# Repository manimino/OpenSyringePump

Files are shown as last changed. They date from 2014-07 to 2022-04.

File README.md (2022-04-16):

# Open Syringe Pump

Deliver small, accurate amounts of liquid. Good for food engineering, CNCs, and bioscience. Cheaper and more flexible than the $1000+ commercial solutions.

This was the first open-source syringe pump, back when 3D printing and open-source hardware took off circa 2015. It saw practical use in many lab and hobby environments. I personally used it in [animal training experiments](https://github.com/manimino/ShrewDriver) to deliver juice rewards.

Successors improved on this design substantially. If you're making a new syringe pump, go find a newer design instead. This repo's for legacy reasons now, to support anyone with one of these pumps.

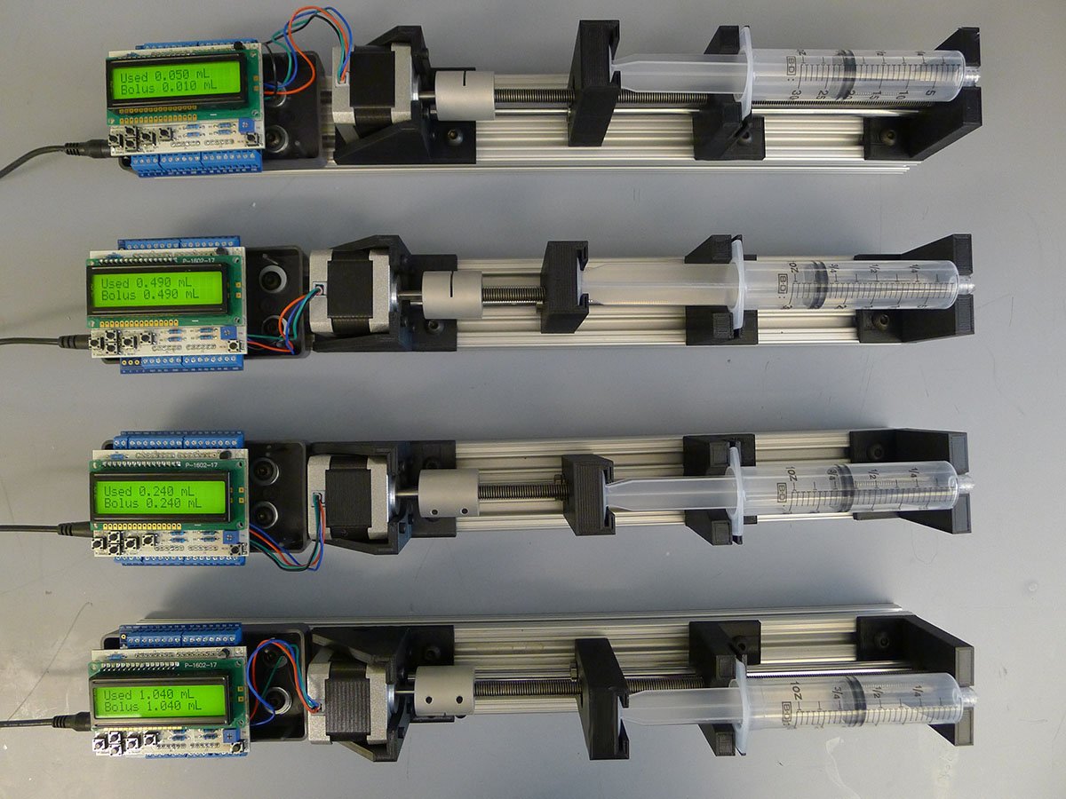
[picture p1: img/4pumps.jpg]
4 syringe pumps

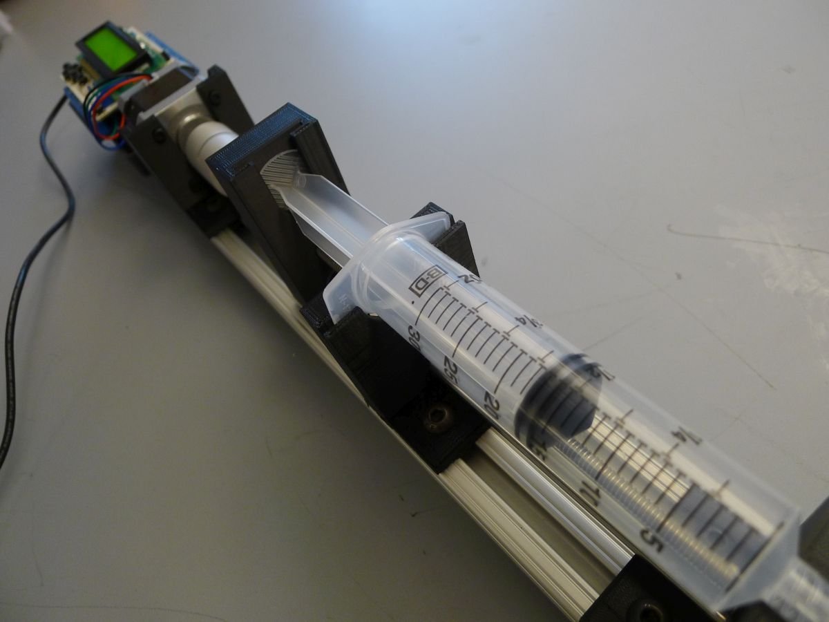
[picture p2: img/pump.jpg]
left side

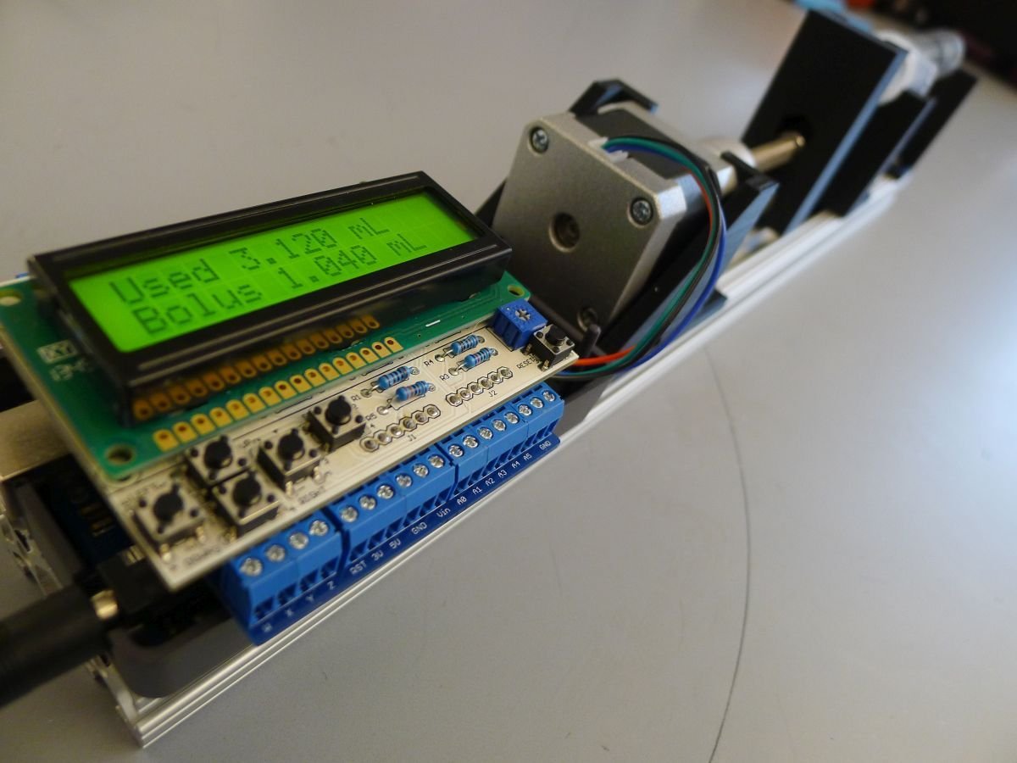
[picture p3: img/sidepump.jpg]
right side


If you want to build one, refer to the [Assembly instructions](instructions.md) and [Electronics + Printing doc](./Syringe%20Pump%20Guide.docx).

## Usage

The face buttons provide manual operation - adjust bolus size and push / pull.

It can be triggered to push and pull liquid via the digital pin inputs, and it accepts more complex commands via serial over USB. 

## Code Layout

'3D files' contains OpenSCAD and STL files for customizing and printing the plastic pieces.

'syringePump' contains the Arduino code.

It requires the AccelStepper library, which you can find in the 'libraries' dir. Copy it into your Arduino\libraries directory to use. You can also get the library from the author's page here: http://www.airspayce.com/mikem/arduino/AccelStepper/

##  Materials

The total cost should come out to about $250 with shipping. So, that's 
substantially cheaper than a commercial syringe pump; they typically go 
for $1000+.

Cost is not the only concern, though. What you get with this thing is:

**- Hackability:** Open-source software and hardware all the way. Customize the hardware and software to do anything you need.

**- Modularity:** You can swap out each component for another one of your choosing. Exceptions and concerns noted below.

**- Extendability:** Want to add [Ethernet]http://arduino.cc/en/Main/ArduinoEthernetShield) or [Bluetooth]http://www.adafruit.com/product/1628)? Both shields are compatible, just stack them on. This [SD card shield]https://www.adafruit.com/product/1141) is compatible too if you want to add data logging. 

**- Ease of assembly:** Minimal soldering required, and tutorials + vendor support are available for most components.

**- Availability of components:**
 Everything's off-the-shelf from stable sources (Adafruit, SparkFun, 
Amazon, McMaster-Carr). If you're in the US, all parts should arrive in 
well under two weeks.

## Electronic Components:

| Purpose                          | Product Link                                                               | Vendor   | Cost (not including shipping) | Notes                                                                                                                      |
|----------------------------------|----------------------------------------------------------------------------|----------|-------------------------------|----------------------------------------------------------------------------------------------------------------------------|
| Microcontroller                  | Arduino Uno R3                                                             | Adafruit | $24.95                        | --                                                                                                                         |
| Stepper Motor                    | NEMA 17 stepper motor, 12V, 1.3A, Holding Torque 40N*cm. Model 42HS4013A4. | Adafruit | $18.50                        | Plenty of power for pushing even thick liquids.                                                                            |
| Stepper Motor Driver             | Big Easy Driver                                                            | Sparkfun | $14.95                        | Attach to digital pins 2 and 3.                                                                                            |
| User Interface Shield            | LCD button shield                                                          | Sparkfun | $12.95                        | Uses digital pins 4 through 9.                                                                                             |
| Power Source                     | 24V 1A power supply                                                        | Jameco   | $11.95                        | --                                                                                                                         |
| Power Switch                     | Inline Power Switch                                                        | Adafruit | $2.50                         | --                                                                                                                         |
| Power Jack                       | Terminal Power Jack                                                        | Adafruit | $2.00                         | --                                                                                                                         |
| Enclosure                        | Arduino Project Enclosure                                                  | Amazon   | $8.95                         | Fits nicely to the Arduino and to the aluminum rail. Only the bottom half is used.                                         |
| Trigger Inputs & Driver Mounting | Proto-Screwshield (Wingshield) R3 Kit for Arduino                          | Adafruit | $14.95                        | A convenient way to expose digital pins so you can send triggers to the syringe pump. Also fits the Easy Driver perfectly. |

## Mechanical Components:

| Purpose                               | Product Link                                                   | Vendor         | Cost (not including shipping) | Notes                                                                                                                                                           |
|---------------------------------------|----------------------------------------------------------------|----------------|-------------------------------|-----------------------------------------------------------------------------------------------------------------------------------------------------------------|
| Mounting Rail                         | 18-inch piece of 1"x2" 80/20 extruded aluminum rail.           | Amazon         | $8.97                         | Mounting everything on the rail makes the project modular and space-efficient. And the 18" length means your syringe pump will fit into most rack mount setups. |
| Motor mount                           | STL + SCAD file (GitHub)                                       |                | --                            | 3D printed                                                                                                                                                      |
| Syringe plunger attachment            | STL + SCAD file (GitHub)                                       |                | --                            | 3D printed                                                                                                                                                      |
| Syringe barrel holder                 | STL + SCAD file (GitHub)                                       |                | --                            | 3D printed                                                                                                                                                      |
| Syringe tip holder                    | STL + SCAD file (GitHub)                                       |                | --                            | 3D printed                                                                                                                                                      |
| Nuts and bolts for attaching to 80/20 | 80/20 Attachment Nuts and Bolts, Economy, 25-pack              | Amazon         | $10.00                        | Cheap and effective.                                                                                                                                            |
| Shaft coupler                         | 5mm - 8mm Rigid Coupling 25x30mm For CNC Stepper Motor ST-RC03 | Stepper Online | $7.47                         | Attaches the stepper motor to the threaded rod.                                                                                                                 |
| Threaded Rod                          | M8 Threaded Rod, Type 316 Stainless Steel, 1m length           | McMaster-Carr  | $14.72                        | Comes as a 1m stick. You'll want to cut this down to around 300mm. There are many ways to do this; I used a chop saw.                                           |
| M8 Nut for Threaded Rod               | M8 Nut, Type 316 Stainless Steel, 50-pack                      | McMaster-Carr  | $13.38                        | --                                                                                                                                                              |
| Smooth rod                            | 8mm rod, 330mm long                                            | Amazon         | $13.39                        | --                                                                                                                                                              |
| Linear Bearing                        | LM8UU 12-pack                                                  | Amazon         | $13.00                        | --                                                                                                                                                              |
| Syringe                               | 30mL syringe 5-pack                                            | Amazon         | $7.99                         | --

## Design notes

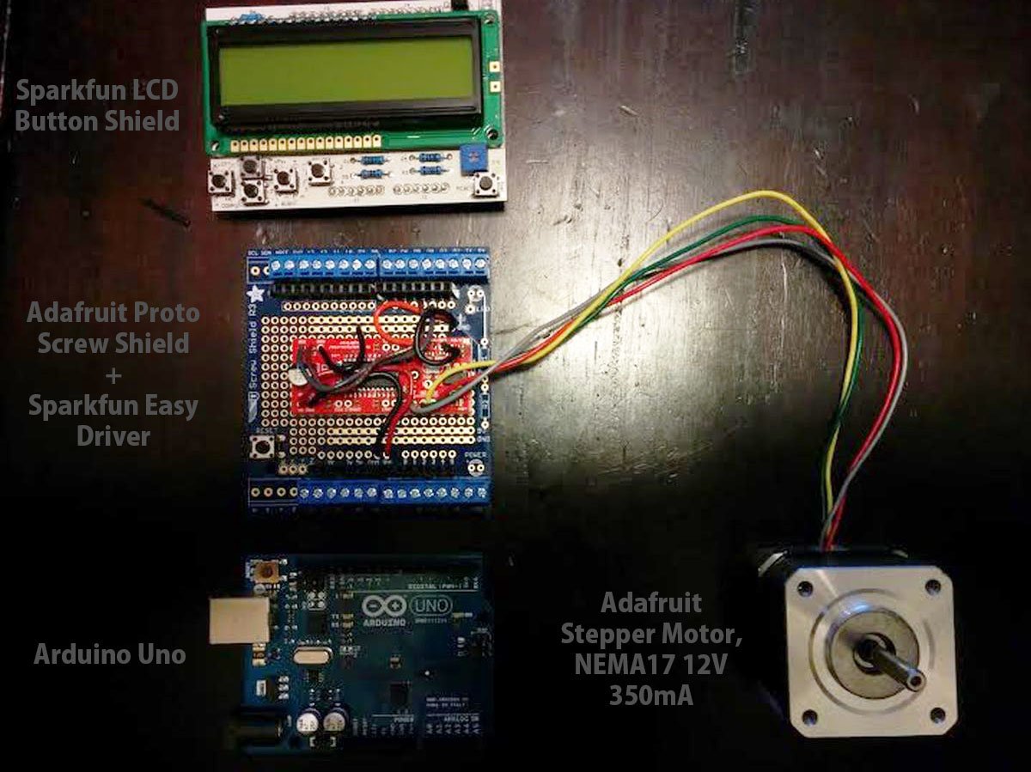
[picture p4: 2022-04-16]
img/electronics.jpg

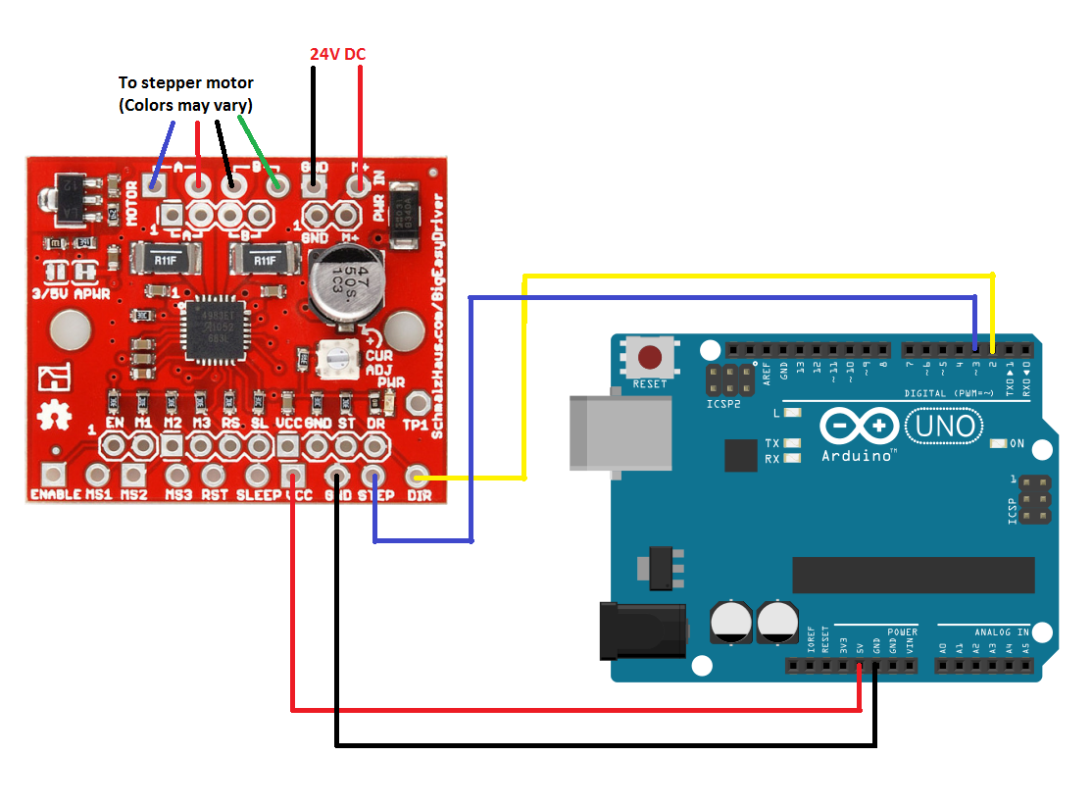
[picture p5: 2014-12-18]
diagrams/24V_BigEasyDriver.png

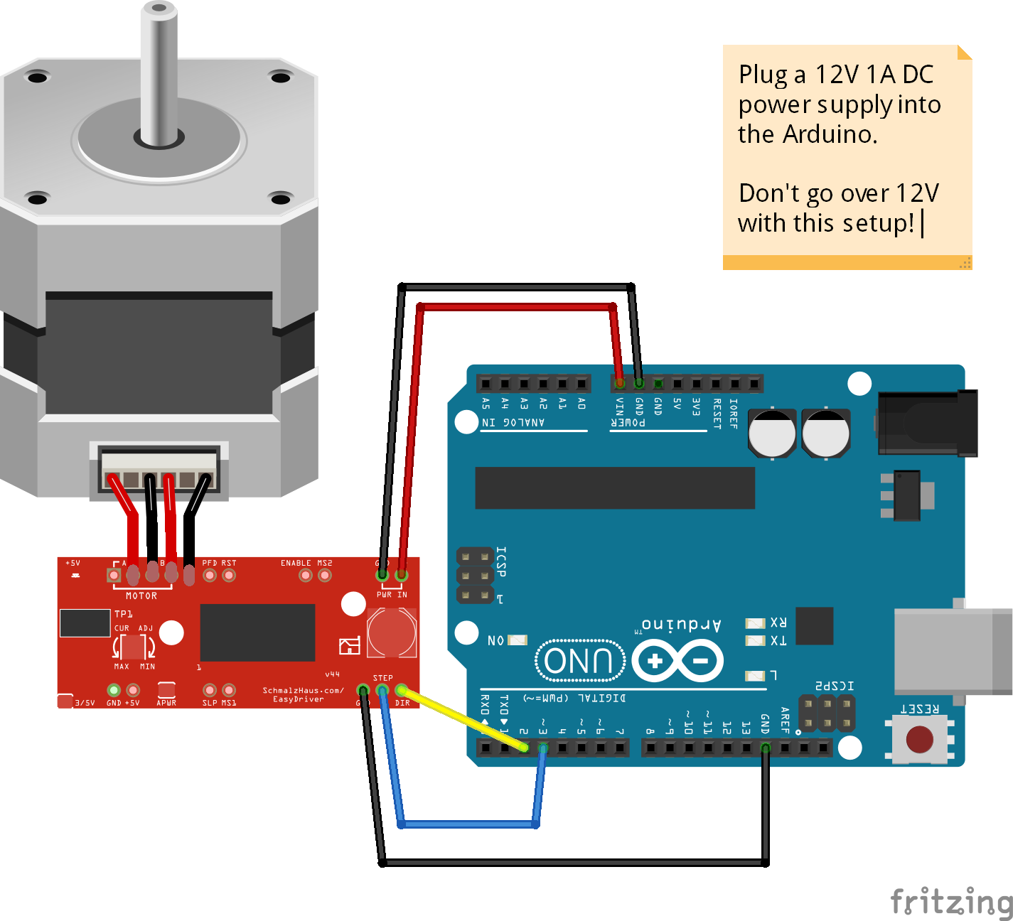
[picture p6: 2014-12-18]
diagrams/12v-easyDriver_bb.png

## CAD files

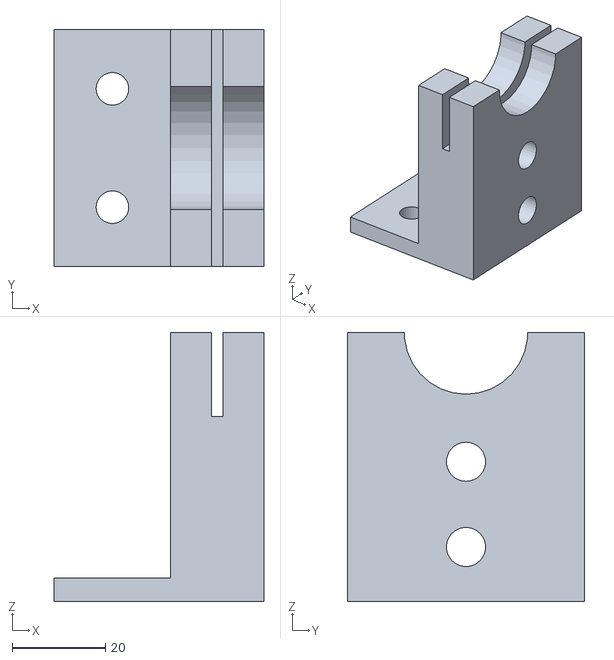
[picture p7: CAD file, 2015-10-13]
3D Files/rodMountBarrel.stl
45.0 x 50.8 x 57.8

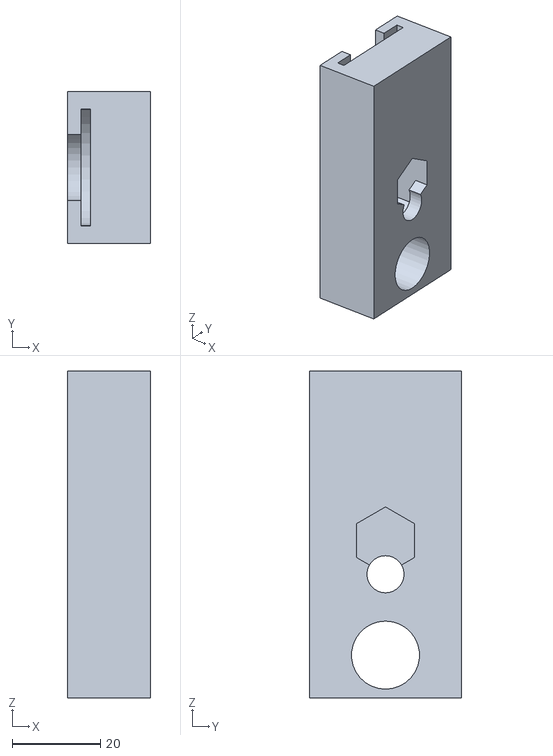
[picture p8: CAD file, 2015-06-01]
3D Files/rodMountPlunger.stl
18.8 x 34.5 x 74.0

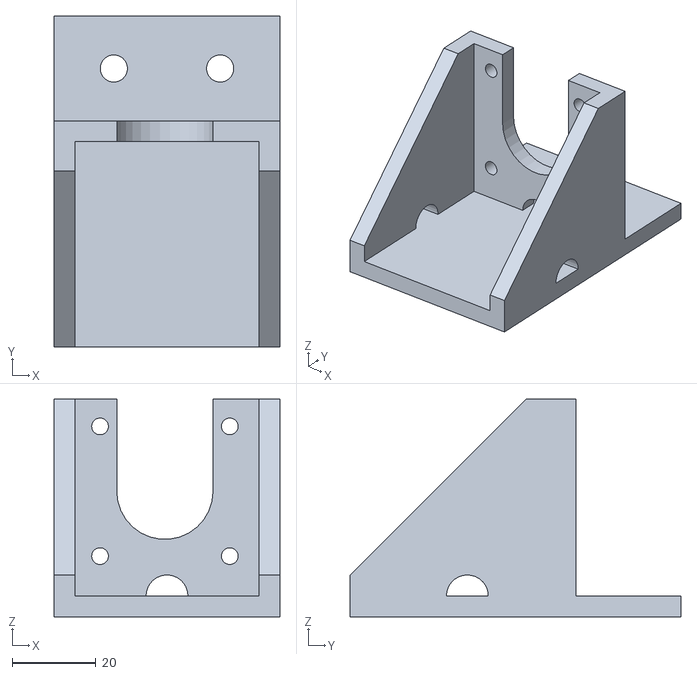
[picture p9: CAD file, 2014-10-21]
3D Files/nemaMount.stl
54.0 x 79.0 x 52.0

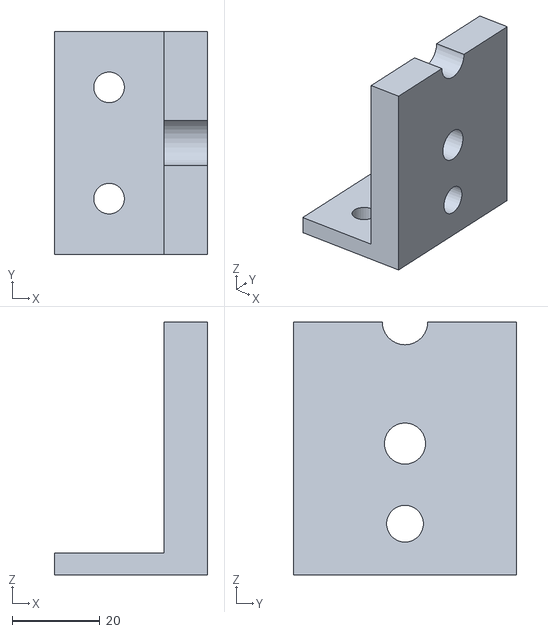
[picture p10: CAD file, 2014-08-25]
3D Files/rodMountSyringe.stl
35.0 x 50.8 x 57.8

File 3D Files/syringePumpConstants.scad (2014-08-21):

/* === Project-universal Constants === */

//Not all of these variables are used in this specific model,
//but the same variable set is used across all models in this project.

$fs = 0.1;

inch = 25.4; //for mm conversion

//width of base
baseSizeY = 2*inch;
centerY = baseSizeY / 2; //both axes go right down the middle of the base

//stepper motor
stepperZSize = 42;
stepperYSize = 42;

//608 bearing 
bearing608Height = 8.5;
bearing608Diameter = 22.5;

//height of holder for 80/20 screws
mountPlateHeight = 5;

//axis heights
threadedAxisHeight = stepperZSize/2 + mountPlateHeight + 4;
smoothAxisHeight = (threadedAxisHeight-6.6) / 2;
smoothRodRadius = 4.2;

//syringe properties
barrelDiameter = 25;

barrelSlotThickness = 3;
barrelSlotHeight = 28;

syringeCenterHeight = threadedAxisHeight + bearing608Diameter/2 + 4 + barrelDiameter/2;

//fixes render oddities
floatCorrection = 0.001; 
floatCorrection2 = 2*floatCorrection; 

//8020 mounting plate
screwPlateSize = 25;	
screwRadius = 3.5;

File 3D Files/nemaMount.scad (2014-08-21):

include <syringePumpConstants.scad>

nema_17_mount();

module nema_17_mount()
{
	wall_thickness = 5;
	motor_width = 42;
	frame_width = motor_width + (wall_thickness + 1)*2;
	bolt = 4;
	height = 25;

	inch = 25.4;
	screwPlateSize = 25;	
	screwRadius = 3.25;
	
	//these are all the mount point holes.
	x1 = -wall_thickness;
	y1 = wall_thickness*2;
	x2 = frame_width+wall_thickness;
	y2 = wall_thickness*2;
	x3 = -wall_thickness;
	y3 = frame_width-wall_thickness*2;
	x4 = frame_width + wall_thickness;
	y4 = frame_width-wall_thickness*2;
	
	//center the whole thing in X
	translate([-frame_width/2, 0, 0])
	{

		//floor, with mounting holes for 80/20
			
		translate([0,-screwPlateSize,-wall_thickness]){
			difference(){
				cube(size=[frame_width,frame_width+screwPlateSize,wall_thickness]);
				
				translate([frame_width/2-inch/2, screwPlateSize/2, 0]){
					cylinder(h=wall_thickness, r=screwRadius);
				}
				translate([frame_width/2+inch/2, screwPlateSize/2, 0]){
					cylinder(h=wall_thickness, r=screwRadius);
				}

			}
		}

		difference()
		{
			//build the main unit.
			union()
			{
				//structure
				cube([wall_thickness, frame_width, frame_width]); //front face
				cube([frame_width, wall_thickness, frame_width]); //left face
				translate([frame_width-wall_thickness, 0, 0])     //right face
					cube([wall_thickness, frame_width, frame_width]);

			}


			//front left mount hole
			echo(x1, y1);
			translate([x1, y1, 0])
			{
				cylinder(r=bolt/2, h=wall_thickness);
				translate([0,0,wall_thickness])
					cylinder(r=bolt, h=wall_thickness*2);
			}
			
			//front right mount hole
			echo(x2, y2);
			translate([x2, y2, 0])
			{
				cylinder(r=bolt/2, h=wall_thickness);
				translate([0,0,wall_thickness])
					cylinder(r=bolt, h=wall_thickness*2);			
			}
			
			//rear left mount hole
			echo(x3, y3);
			translate([x3, y3, 0])
			{
				cylinder(r=bolt/2, h=wall_thickness);
				translate([0,0,wall_thickness])
					cylinder(r=bolt, h=wall_thickness*2);
			}
			
			//rear right mount hole
			echo(x4, y4);
			translate([x4, y4, 0])
			{
				cylinder(r=bolt/2, h=wall_thickness);
				translate([0,0,wall_thickness])
					cylinder(r=bolt, h=wall_thickness*2);
			}
			
			//mount hole slits
			translate([frame_width + wall_thickness*1.5, frame_width-wall_thickness*2, wall_thickness/2])
				cube(size=[wall_thickness, 0.1, wall_thickness*3], center=true);
			translate([frame_width + wall_thickness*1.5, wall_thickness*2, wall_thickness/2])
				cube(size=[wall_thickness, 0.1, wall_thickness*3], center=true);
			translate([-wall_thickness*1.5, frame_width-wall_thickness*2, wall_thickness/2])
				cube(size=[wall_thickness, 0.1, wall_thickness*3], center=true);
			translate([-wall_thickness*1.5, wall_thickness*2, wall_thickness/2])
				cube(size=[wall_thickness, 0.1, wall_thickness*3], center=true);

			//nema 17 mount
			rotate([90, 0, 0])
			{
				translate([frame_width/2+0.5, height, -wall_thickness])
				{
					translate([15.5, 15.5, 0])
						cylinder(r=bolt/2, h=wall_thickness+1);
					translate([-15.5, 15.5, 0])
						cylinder(r=bolt/2, h=wall_thickness+1);
					translate([15.5, -15.5, 0])
						cylinder(r=bolt/2, h=wall_thickness+1);
					translate([-15.5, -15.5, 0])
						cylinder(r=bolt/2, h=wall_thickness+1);

					cylinder(r=11.5, h=wall_thickness+1);

					translate([-11.5, 0, 0])
						cube([23, frame_width, wall_thickness+1]);
				}
			}

			//back slant cutaway
			translate([0, 0, frame_width+wall_thickness])
				rotate([45, 0, 0])
					translate([-frame_width, 0, -frame_width*2])
						cube(size=[frame_width*4, frame_width*2, frame_width*4]);

			//front anti-warp circle
			translate([frame_width/2, wall_thickness*1.25, 0])
				rotate([90, 0, 0])
					cylinder(r=wall_thickness, h=wall_thickness*2);

			//middle anti-warp circle			
			translate([0, motor_width/2 + wall_thickness, 0])
				rotate([0, 90, 0])
					cylinder(r=wall_thickness, h=frame_width+1);

			//cutout / tidy up cubes.
			translate([wall_thickness, wall_thickness-0.1, -1])
				cube([frame_width-wall_thickness*2, frame_width-wall_thickness, motor_width*2]);
			translate([-frame_width/2,-frame_width/2, wall_thickness+motor_width])
				cube([frame_width*2, frame_width*2, frame_width]);
			translate([-frame_width/2, -frame_width/2,-frame_width])
				cube([frame_width*2, frame_width*2, frame_width]);
		}
	}
}

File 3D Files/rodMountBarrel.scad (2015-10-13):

include <syringePumpConstants.scad>

/* === Model-specific Constants === */

//cube containing rods and syringe barrel stop
mountXSize = 20;
mountZSize = syringeCenterHeight;

//slot parameters
plungerDiameter = 26.5;
barrelSlotThickness = 2.5;
barrelSlotOffset = mountXSize/2 - barrelSlotThickness/2;
barrelSlotHeight = 36;

/* === Model === */

//main cube, holds the two axes
difference(){
	cube(size=[mountXSize,baseSizeY,mountZSize]);

	//608 bearing for threaded rod
	translate([-floatCorrection,centerY,threadedAxisHeight]){
		rotate(a=[0,90,0]){
			nutWell();
		}
	}
	
	//bore hole for threaded rod
	translate([-floatCorrection,centerY,threadedAxisHeight]){
		rotate(a=[0,90,0]){
			cylinder(h=mountXSize+floatCorrection2, r=smoothRodRadius);
		}
	}

	//hole for smooth rod (needs to fit fairly tight)
	translate([-floatCorrection,centerY,smoothAxisHeight]){
		rotate(a=[0,90,0]){
			cylinder(h=mountXSize+floatCorrection2, r=smoothRodRadius);
		}
	}

	//hole for syringe barrel top to go in
	translate([barrelSlotOffset,centerY,syringeCenterHeight]){
		translate([0,-baseSizeY/2,-barrelSlotHeight/2]){
			cube(size=[barrelSlotThickness, baseSizeY, barrelSlotHeight]);
		}
	}	
	translate([-floatCorrection,centerY,syringeCenterHeight]){
		rotate(a=[0,90,0]){
			cylinder(h=mountXSize+floatCorrection2, r=plungerDiameter/2);
		}	
		translate([0,-plungerInnerDiameter/2,0]){
			cube(size=[barrelSlotThickness+floatCorrection2,plungerInnerDiameter,mountZSize]);
		}
	}	
	
}

// 80/20 screw plate
difference(){
	translate([-screwPlateSize,0,0]){
		cube(size=[screwPlateSize,baseSizeY,mountPlateHeight]);
	}

	translate([-screwPlateSize/2,baseSizeY/4,0]){
		cylinder(h=mountPlateHeight, r=screwRadius);
	}
	translate([-screwPlateSize/2,3*baseSizeY/4,0]){
		cylinder(h=mountPlateHeight, r=screwRadius);
	}

}

module bearing608(){
	cylinder(h=bearing608Height, r=bearing608Diameter/2);	
}

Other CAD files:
3D Files/rodMountPlunger.scad
3D Files/rodMountSyringe.scad

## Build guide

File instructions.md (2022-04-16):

# Assembly

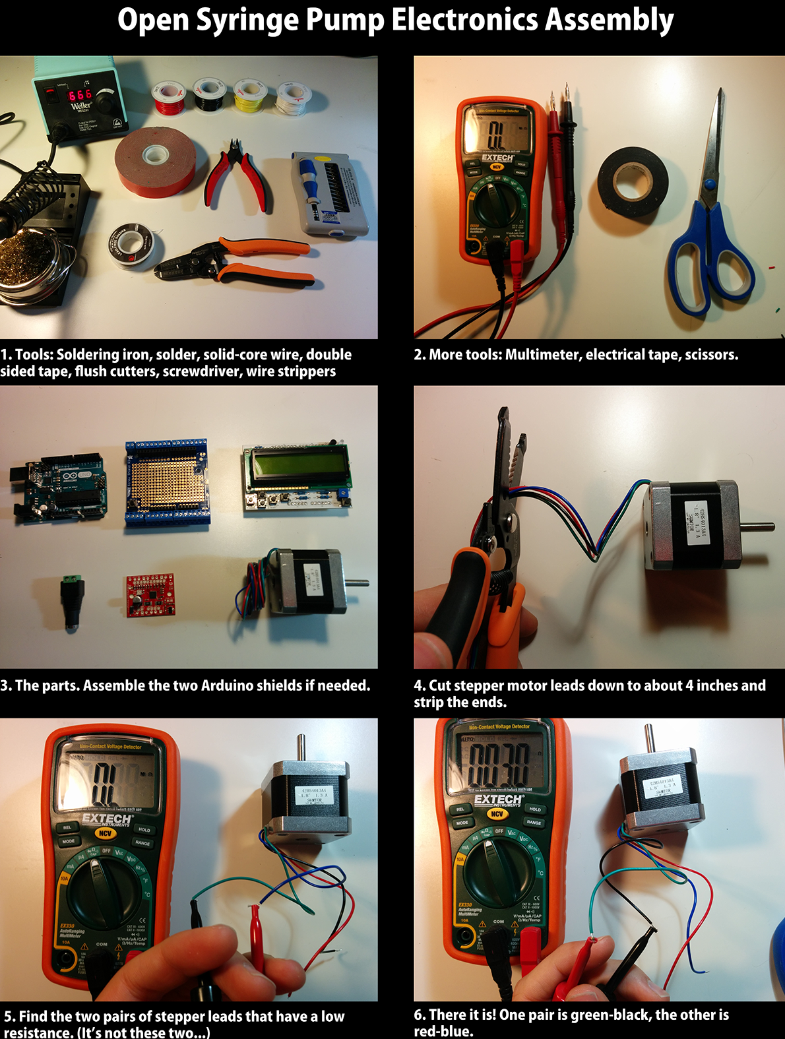
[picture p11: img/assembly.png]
assembly steps


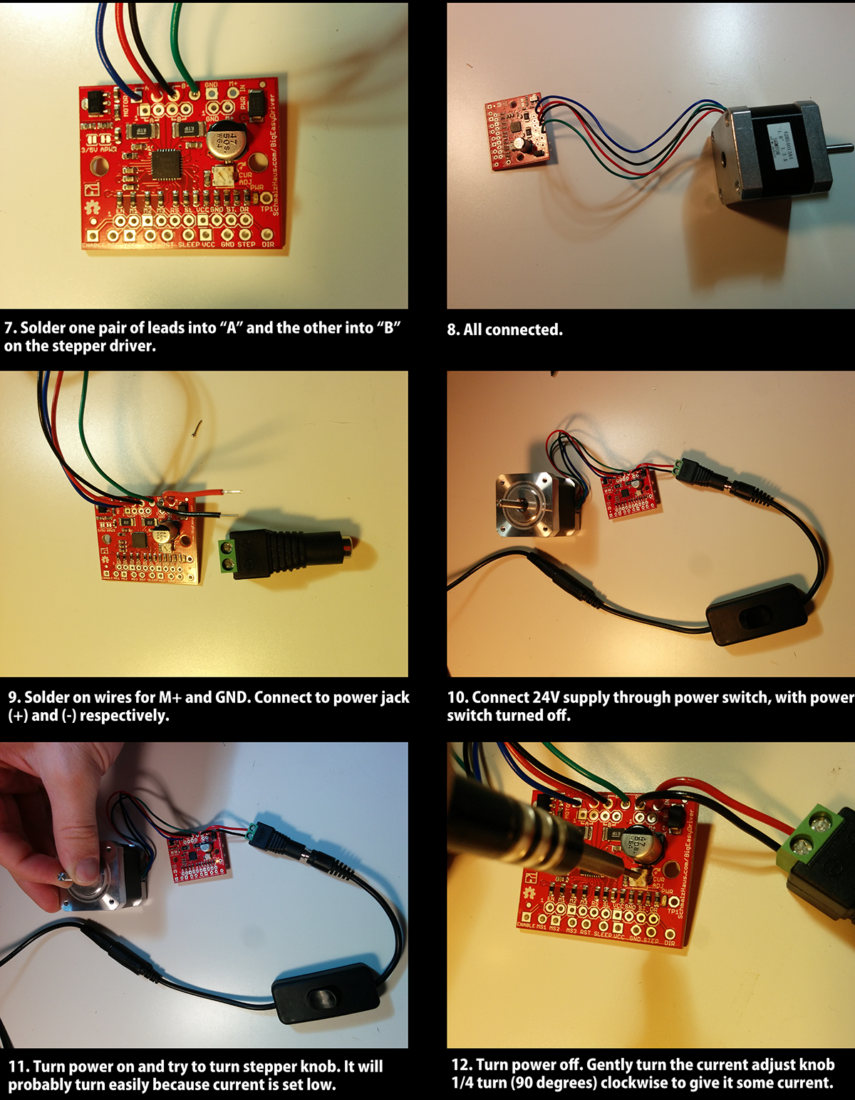
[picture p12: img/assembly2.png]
assembly steps


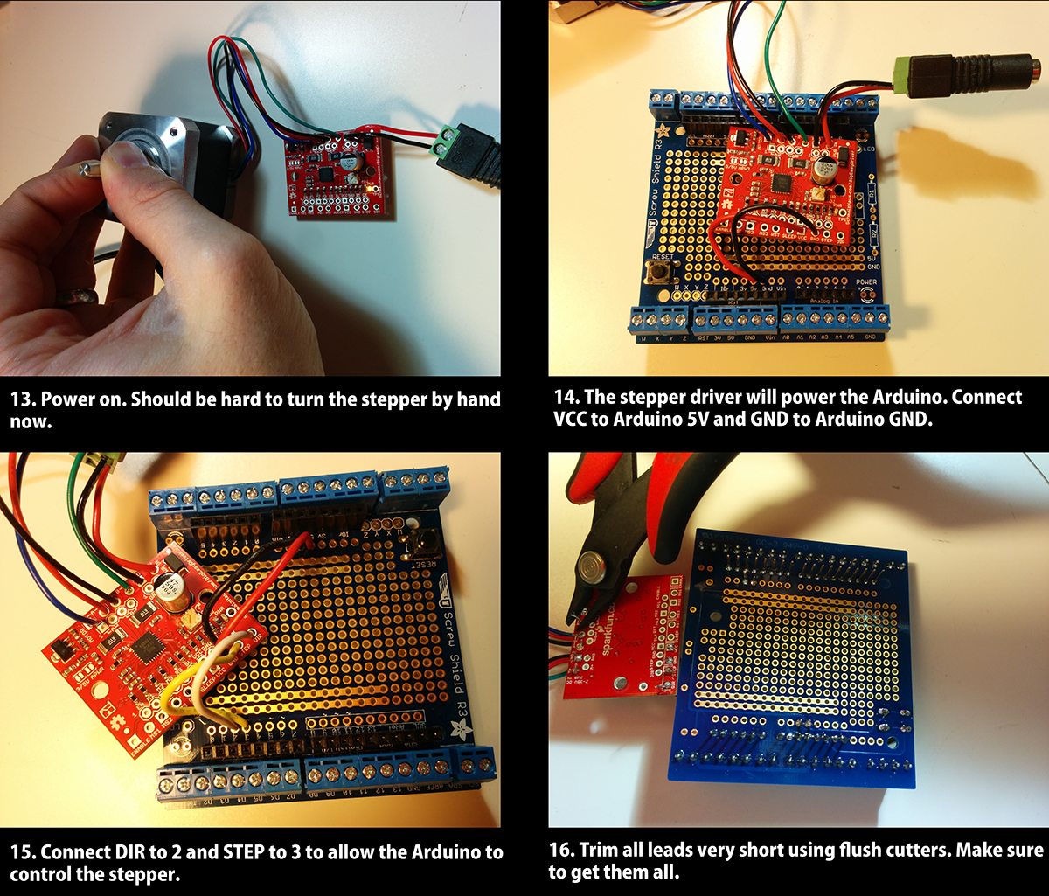
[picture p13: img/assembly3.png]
assembly steps


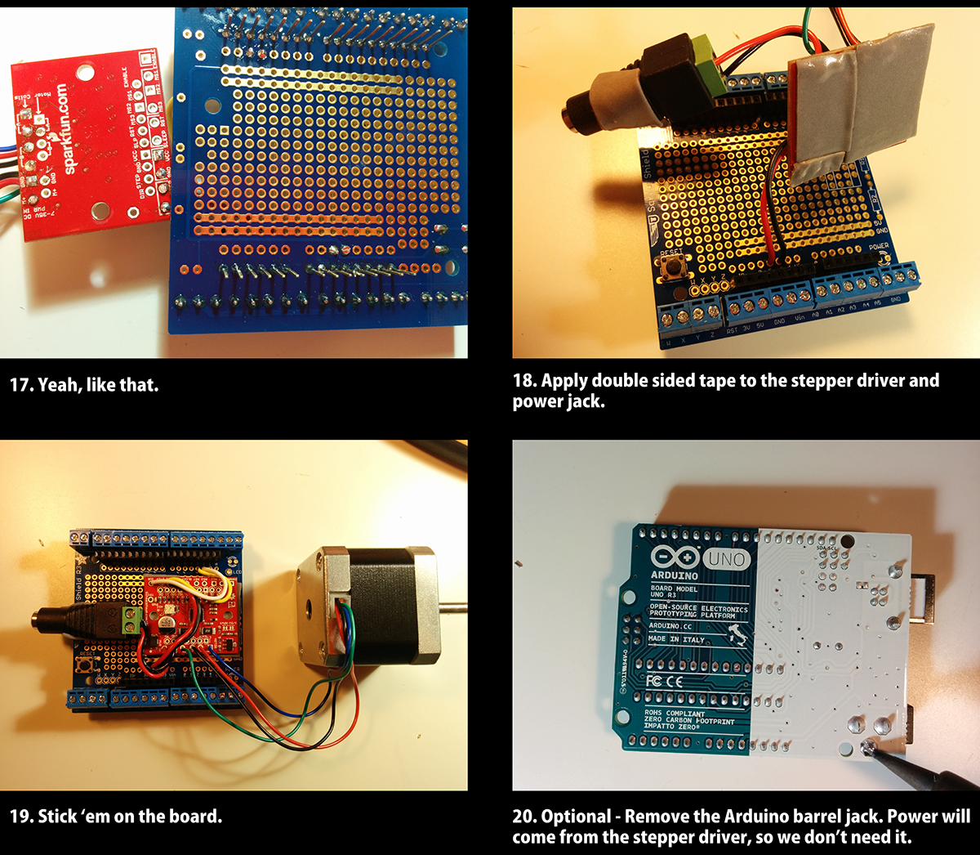
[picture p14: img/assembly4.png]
assembly steps


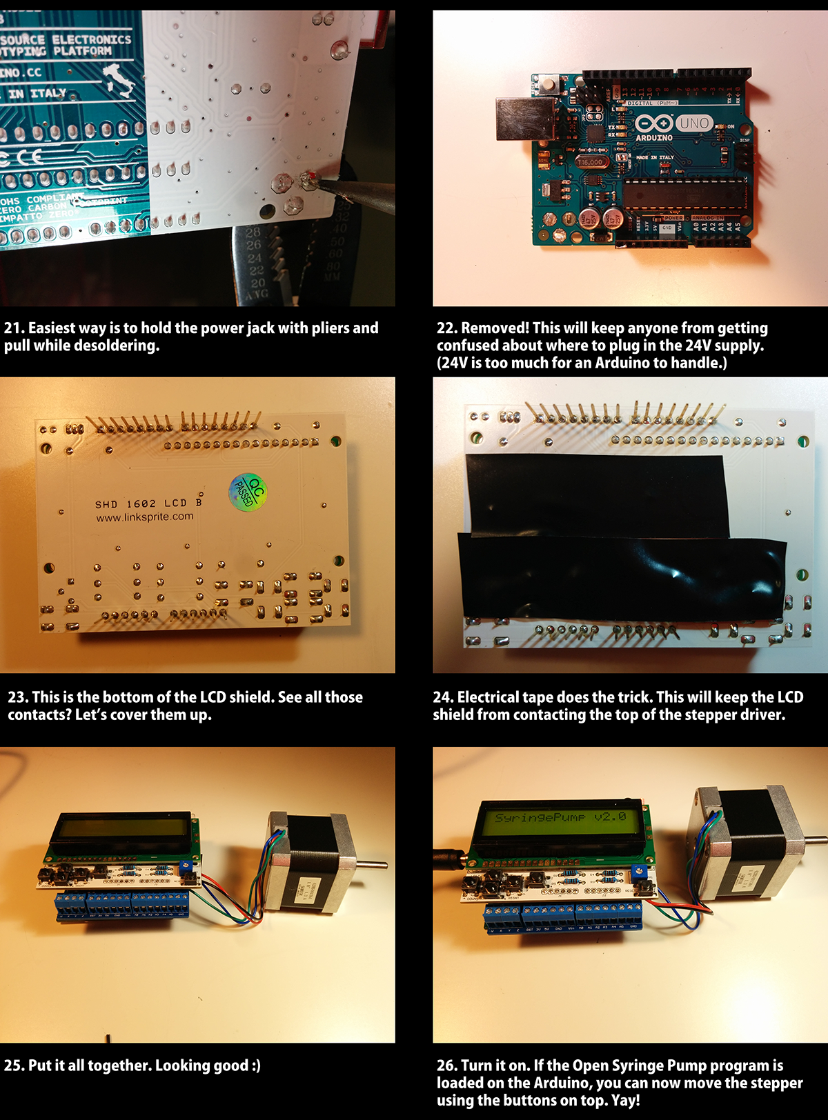
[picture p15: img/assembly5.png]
assembly steps


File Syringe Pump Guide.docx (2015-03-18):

Syringe Pump Guide

Building Syringe Pumps:

Once you have all the parts, building it is pretty intuitive. See full instructions at http://hackaday.io/project/1838-Open-Syringe-Pump.

Even if you’re inexperienced at soldering, this is a great project to learn on! Solder the Arduino shield kits first as practice, then solder the wires onto the Big Easy Driver.

Probably the only difficult part of the assembly is to cut the threaded rod and smooth rod to the appropriate length. You can either do that yourself with a chop saw by clamping the rod into the groove of the 80/20 rail. Or you can bring it to a machine shop and have it cut there (should be quite cheap).

Programming

To change the firmware of the syringe pump, connect it to your computer using a USB cable.

You will need the Arduino IDE : http://www.arduino.cc/en/Main/Software

The code is available from here: https://github.com/naroom/OpenSyringePump (see “Download As Zip” on the right side.)

First, open the SyringePump.ino file:

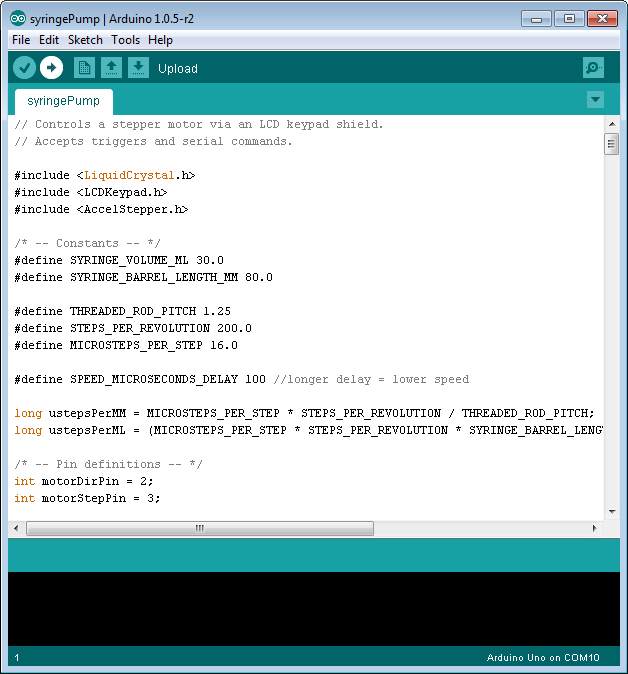
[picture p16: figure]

Click “Upload” to compile and run the code on the syringe pump. Note that you may want to change the numbers pertaining to your specific syringe (SYRINGE_VOLUME_ML and SYRINGE_BARREL_LENGTH_MM).

You can also customize the code to change the speed, default bolus size, add more menu options, add more commands – anything you like!

You can send commands to the serial port directly from the Arduino IDE. Use Tools -> Serial Monitor:

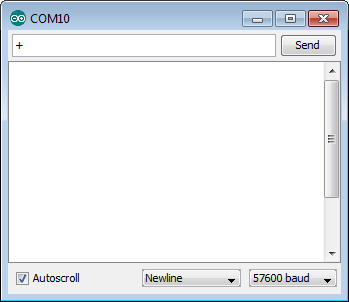
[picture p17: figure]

Change the baudrate to 57600 and set the line terminator to “Newline” as pictured. Then try sending a “+” as shown. If the syringe pump is powered, it will send a bolus. Sending “-“ will reverse the pump by 1 bolus. You can also specify the bolus size in microliters by sending it, e.g. ‘300’ will set it to 300 microliter bolus.

Driver Chip Documentation

This is a nice writeup about using the Big Easy Driver: http://bildr.org/2012/11/big-easy-driver-arduino/

Note the power adjustment knob in the first diagram – if the motor’s overheating, turn it down. For more power, turn it up! Note that the knob is fragile. Use a large screwdriver and turn it very gently.

3D Printing

Want to customize the project to fit your syringe? No problem! The 3D print files included can be opened using the free program OpenSCAD: http://www.openscad.org/ Load a file and press F6 to render it. Change parameters as you see fit!

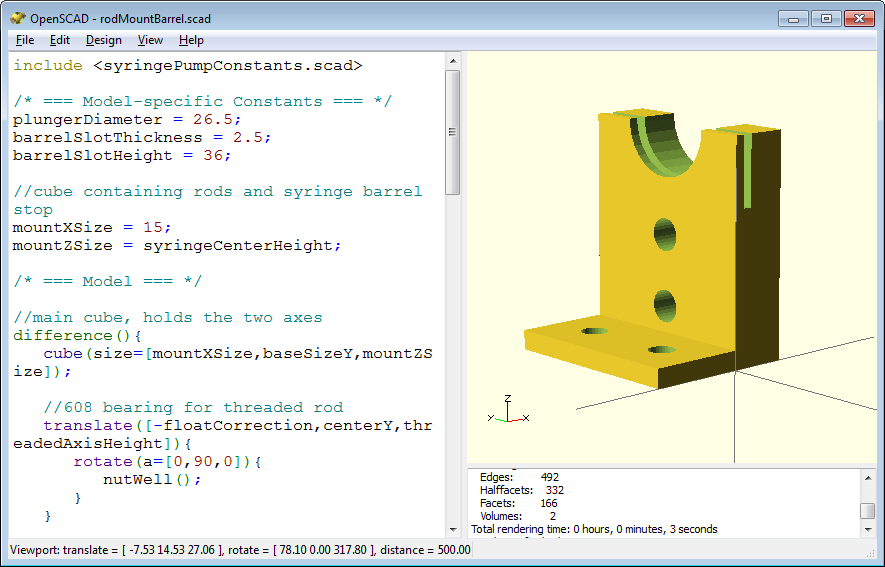
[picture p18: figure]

OpenSCAD has fantastic documentation and is very fun to learn: http://www.openscad.org/documentation.html

When you are done making your model in OpenSCAD, use the “Export As STL” menu option to get a 3D printable file.

Wiring

There are two ways to wire it, depending on which driver you go with. I prefer to use a 24V power supply in this fashion:

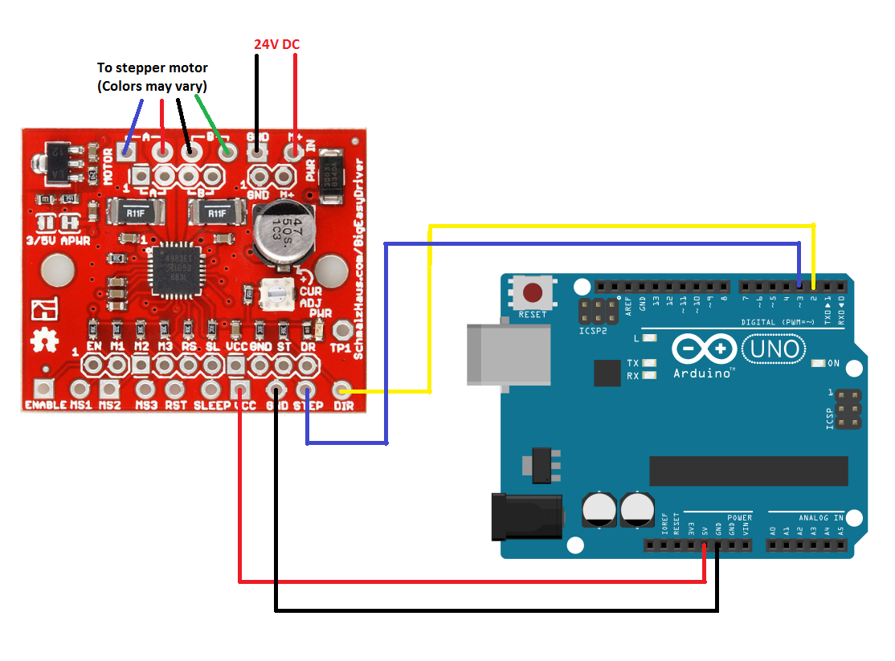
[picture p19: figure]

But you can also do it by plugging 12V directly into the Arduino. This shows the SparkFun EasyDriver, but you can also use the Big Easy Driver here:


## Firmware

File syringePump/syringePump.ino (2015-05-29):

// Controls a stepper motor via an LCD keypad shield.
// Accepts triggers and serial commands.
// To run, you will need the LCDKeypad library installed - see libraries dir.

// Serial commands:
// Set serial baud rate to 57600 and terminate commands with newlines.
// Send a number, e.g. "100", to set bolus size.
// Send a "+" to push that size bolus.
// Send a "-" to pull that size bolus.

#include <LiquidCrystal.h>
#include <LCDKeypad.h>

/* -- Constants -- */
#define SYRINGE_VOLUME_ML 30.0
#define SYRINGE_BARREL_LENGTH_MM 80.0

#define THREADED_ROD_PITCH 1.25
#define STEPS_PER_REVOLUTION 200.0
#define MICROSTEPS_PER_STEP 16.0

#define SPEED_MICROSECONDS_DELAY 100 //longer delay = lower speed

long ustepsPerMM = MICROSTEPS_PER_STEP * STEPS_PER_REVOLUTION / THREADED_ROD_PITCH;
long ustepsPerML = (MICROSTEPS_PER_STEP * STEPS_PER_REVOLUTION * SYRINGE_BARREL_LENGTH_MM) / (SYRINGE_VOLUME_ML * THREADED_ROD_PITCH );

/* -- Pin definitions -- */
int motorDirPin = 2;
int motorStepPin = 3;

int triggerPin = A3;
int bigTriggerPin = A4;

/* -- Keypad states -- */
int  adc_key_val[5] ={30, 150, 360, 535, 760 };

enum{ KEY_RIGHT, KEY_UP, KEY_DOWN, KEY_LEFT, KEY_SELECT, KEY_NONE};
int NUM_KEYS = 5;
int adc_key_in;
int key = KEY_NONE;

/* -- Enums and constants -- */
enum{PUSH,PULL}; //syringe movement direction
enum{MAIN, BOLUS_MENU}; //UI states

const int mLBolusStepsLength = 9;
float mLBolusSteps[9] = {0.001, 0.005, 0.010, 0.050, 0.100, 0.500, 1.000, 5.000, 10.000};

/* -- Default Parameters -- */
float mLBolus = 0.500; //default bolus size
float mLBigBolus = 1.000; //default large bolus size
float mLUsed = 0.0;
int mLBolusStepIdx = 3; //0.05 mL increments at first
float mLBolusStep = mLBolusSteps[mLBolusStepIdx];

long stepperPos = 0; //in microsteps
char charBuf[16];

//debounce params
long lastKeyRepeatAt = 0;
long keyRepeatDelay = 400;
long keyDebounce = 125;
int prevKey = KEY_NONE;
        
//menu stuff
int uiState = MAIN;

//triggering
int prevBigTrigger = HIGH;
int prevTrigger = HIGH;

//serial
String serialStr = "";
boolean serialStrReady = false;

/* -- Initialize libraries -- */
LiquidCrystal lcd(8, 13, 9, 4, 5, 6, 7);

void setup(){
  /* LCD setup */  
  lcd.begin(16, 2);
  lcd.clear();

  lcd.print("SyringePump v2.0");

  /* Triggering setup */
  pinMode(triggerPin, INPUT);
  pinMode(bigTriggerPin, INPUT);
  digitalWrite(triggerPin, HIGH); //enable pullup resistor
  digitalWrite(bigTriggerPin, HIGH); //enable pullup resistor
  
  /* Motor Setup */ 
  pinMode(motorDirPin, OUTPUT);
  pinMode(motorStepPin, OUTPUT);
  
  /* Serial setup */
  //Note that serial commands must be terminated with a newline
  //to be processed. Check this setting in your serial monitor if 
  //serial commands aren't doing anything.
  Serial.begin(57600); //Note that your serial connection must be set to 57600 to work!
}

void loop(){
  //check for LCD updates
  readKey();
  
  //look for triggers on trigger lines
  checkTriggers();
  
  //check serial port for new commands
  readSerial();
	if(serialStrReady){
		processSerial();
	}
}

void checkTriggers(){
		//check low-reward trigger line
    int pushTriggerValue = digitalRead(triggerPin);
    if(pushTriggerValue == HIGH && prevTrigger == LOW){
      bolus(PUSH);
			updateScreen();
    }
    prevTrigger = pushTriggerValue;
    
		//check high-reward trigger line
    int bigTriggerValue = digitalRead(bigTriggerPin);
    if(bigTriggerValue == HIGH && prevBigTrigger == LOW){
			//push big reward amount
			float mLBolusTemp = mLBolus;
			mLBolus = mLBigBolus;
			bolus(PUSH);
			mLBolus = mLBolusTemp;

			updateScreen();
    }
    prevBigTrigger = bigTriggerValue;
}

void readSerial(){
		//pulls in characters from serial port as they arrive
		//builds serialStr and sets ready flag when newline is found
		while (Serial.available()) {
			char inChar = (char)Serial.read(); 
			if (inChar == '\n') {
				serialStrReady = true;
			} 
                        else{
			  serialStr += inChar;
                        }
		}
}

void processSerial(){
	//process serial commands as they are read in
	if(serialStr.equals("+")){
		bolus(PUSH);
		updateScreen();
	}
	else if(serialStr.equals("-")){
		bolus(PULL);
		updateScreen();
	}
        else if(serialStr.toInt() != 0){
          int uLbolus = serialStr.toInt();
          mLBolus = (float)uLbolus / 1000.0;
          updateScreen();
        }
        else{
           Serial.write("Invalid command: ["); 
           char buf[40];
           serialStr.toCharArray(buf, 40);
           Serial.write(buf); 
           Serial.write("]\n"); 
        }
        serialStrReady = false;
	serialStr = "";
}

void bolus(int direction){
        //Move stepper. Will not return until stepper is done moving.        
  
	//change units to steps
	long steps = (mLBolus * ustepsPerML);
	if(direction == PUSH){
                digitalWrite(motorDirPin, HIGH);
		steps = mLBolus * ustepsPerML;
		mLUsed += mLBolus;
	}
	else if(direction == PULL){
                digitalWrite(motorDirPin, LOW);
		if((mLUsed-mLBolus) > 0){
			mLUsed -= mLBolus;
		}
		else{
			mLUsed = 0;
		}
	}	

      float usDelay = SPEED_MICROSECONDS_DELAY; //can go down to 20 or 30
    
      for(long i=0; i < steps; i++){ 
        digitalWrite(motorStepPin, HIGH); 
        delayMicroseconds(usDelay); 
    
        digitalWrite(motorStepPin, LOW); 
        delayMicroseconds(usDelay); 
      } 

}

void readKey(){
	//Some UI niceness here. 
        //When user holds down a key, it will repeat every so often (keyRepeatDelay).
        //But when user presses and releases a key, 
        //the key becomes responsive again after the shorter debounce period (keyDebounce).

	adc_key_in = analogRead(0);
	key = get_key(adc_key_in); // convert into key press

	long currentTime = millis();
        long timeSinceLastPress = (currentTime-lastKeyRepeatAt);
        
        boolean processThisKey = false;
	if (prevKey == key && timeSinceLastPress > keyRepeatDelay){
          processThisKey = true;
        }
        if(prevKey == KEY_NONE && timeSinceLastPress > keyDebounce){
          processThisKey = true;
        }
        if(key == KEY_NONE){
          processThisKey = false;
        }  
        
        prevKey = key;
        
        if(processThisKey){
          doKeyAction(key);
  	  lastKeyRepeatAt = currentTime;
        }
}

void doKeyAction(unsigned int key){
	if(key == KEY_NONE){
        return;
    }

	if(key == KEY_SELECT){
		if(uiState == MAIN){
			uiState = BOLUS_MENU;
		}
		else if(BOLUS_MENU){
			uiState = MAIN;
		}
	}

	if(uiState == MAIN){
		if(key == KEY_LEFT){
			bolus(PULL);
		}
		if(key == KEY_RIGHT){
			bolus(PUSH);
		}
		if(key == KEY_UP){
			mLBolus += mLBolusStep;
		}
		if(key == KEY_DOWN){
			if((mLBolus - mLBolusStep) > 0){
			  mLBolus -= mLBolusStep;
			}
			else{
			  mLBolus = 0;
			}
		}
	}
	else if(uiState == BOLUS_MENU){
		if(key == KEY_LEFT){
			//nothin'
		}
		if(key == KEY_RIGHT){
			//nothin'
		}
		if(key == KEY_UP){
			if(mLBolusStepIdx < mLBolusStepsLength-1){
				mLBolusStepIdx++;
				mLBolusStep = mLBolusSteps[mLBolusStepIdx];
			}
		}
		if(key == KEY_DOWN){
			if(mLBolusStepIdx > 0){
				mLBolusStepIdx -= 1;
				mLBolusStep = mLBolusSteps[mLBolusStepIdx];
			}
		}
	}

	updateScreen();
}

void updateScreen(){
	//build strings for upper and lower lines of screen
	String s1; //upper line
	String s2; //lower line
	
	if(uiState == MAIN){
		s1 = String("Used ") + decToString(mLUsed) + String(" mL");
		s2 = (String("Bolus ") + decToString(mLBolus) + String(" mL"));		
	}
	else if(uiState == BOLUS_MENU){
		s1 = String("Menu> BolusStep");
		s2 = decToString(mLBolusStep);
	}

	//do actual screen update
	lcd.clear();

	s2.toCharArray(charBuf, 16);
	lcd.setCursor(0, 1);  //line=2, x=0
	lcd.print(charBuf);
	
	s1.toCharArray(charBuf, 16);
	lcd.setCursor(0, 0);  //line=1, x=0
	lcd.print(charBuf);
}


// Convert ADC value to key number
int get_key(unsigned int input){
  int k;
  for (k = 0; k < NUM_KEYS; k++){
    if (input < adc_key_val[k]){
      return k;
    }
  }
  if (k >= NUM_KEYS){
    k = KEY_NONE;     // No valid key pressed
  }
  return k;
}

String decToString(float decNumber){
	//not a general use converter! Just good for the numbers we're working with here.
	int wholePart = decNumber; //truncate
	int decPart = round(abs(decNumber*1000)-abs(wholePart*1000)); //3 decimal places
        String strZeros = String("");
        if(decPart < 10){
          strZeros = String("00");
        }  
        else if(decPart < 100){
          strZeros = String("0");
        }
	return String(wholePart) + String('.') + strZeros + String(decPart);
}

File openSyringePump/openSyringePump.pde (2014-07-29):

// Controls a stepper motor via an LCD keypad shield.

#include <LCD4Bit_mod.h> 
#include <AccelStepper.h>

/* -- Constants -- */
#define SYRINGE_VOLUME_ML 30.0
#define SYRINGE_BARREL_LENGTH_MM 80.0

#define THREADED_ROD_PITCH 1.25
#define STEPS_PER_REVOLUTION 200.0
#define MICROSTEPS_PER_STEP 16.0

long ustepsPerMM = MICROSTEPS_PER_STEP * STEPS_PER_REVOLUTION / THREADED_ROD_PITCH;
long ustepsPerML = (MICROSTEPS_PER_STEP * STEPS_PER_REVOLUTION * SYRINGE_BARREL_LENGTH_MM) / (SYRINGE_VOLUME_ML * THREADED_ROD_PITCH );

/* -- Pin definitions -- */
int motorDirPin = 2;
int motorStepPin = 3;
int triggerPin = A3;

//Key states
//int  adc_key_val[5] ={30, 150, 360, 535, 760 };
int  adc_key_val[5] ={50, 180, 400, 575, 800 };


enum{ KEY_RIGHT, KEY_UP, KEY_DOWN, KEY_LEFT, KEY_SELECT, KEY_NONE};
int NUM_KEYS = 5;
int adc_key_in;
int key=-1;
int oldkey=-1;

//various enums
enum{PUSH,PULL}; //syringe movement direction
enum{MAIN, BOLUS_MENU}; //UI states

const int mLBolusStepsLength = 9;
float mLBolusSteps[9] = {0.001, 0.005, 0.010, 0.050, 0.100, 0.500, 1.000, 5.000, 10.000};

/* -- Default Parameters -- */
int motorSpeed = 4000; //maximum steps per second
int motorAccel = 80000; //steps/second/second to accelerate

float mLBolus = 0.1;
float mLUsed = 0.0;
int mLBolusStepIdx = 3; //0.05 mL increments at first
float mLBolusStep = mLBolusSteps[mLBolusStepIdx];

long stepperPos = 0; //in microsteps
char charBuf[16];

//debounce params
int lastTick = 0;
int debounceTime = 50;

//menu stuff
int uiState = MAIN;

//triggering
int prevTrigger = LOW;

/* -- Initialize libraries -- */
AccelStepper stepper(1, motorStepPin, motorDirPin); //the "1" tells it we are using a driver
LCD4Bit_mod lcd = LCD4Bit_mod(2); 

void setup(){
  /* LCD setup */  
  lcd.init();
  lcd.clear();

  lcd.printIn("SyringePump v0.1");
  lastTick = millis();

  /* Stepper setup */
  stepper.setMaxSpeed(motorSpeed);
  stepper.setSpeed(motorSpeed);
  stepper.setAcceleration(motorAccel);
  
  /* Triggering setup */
  pinMode(triggerPin, INPUT);
}

void loop(){
  //update stepper position
  stepper.run();

  //check for LCD updates
  readKey();
  
  //look for trigger on trigger line
  checkTrigger();
}


void checkTrigger(){
    int triggerValue = digitalRead(triggerPin);
    if(triggerValue == HIGH && prevTrigger == LOW){
      bolus(PUSH);
    }
    prevTrigger = triggerValue;
}

void bolus(int direction){
	//change units to steps
	long steps;
	if(direction == PUSH){
		steps = mLBolus * ustepsPerML;
		mLUsed += mLBolus;
	}
	else if(direction == PULL){
		steps = -mLBolus * ustepsPerML;
		if((mLUsed-mLBolus) > 0){
			mLUsed -= mLBolus;
		}
		else{
			mLUsed = 0;
		}
	}	
	stepperPos += steps;
	stepper.moveTo(stepperPos);
}

void readKey(){
	//don't poll too often
	long currentTime = millis();
	if ((currentTime-lastTick) < debounceTime){
		return;
	}
	
	lastTick = currentTime;
	adc_key_in = analogRead(0);
	key = get_key(adc_key_in); // convert into key press

	if (key != oldkey){
	if (oldkey == KEY_NONE || key == KEY_NONE){
			oldkey = key;
			doKeyAction(key);
		}
		else{
			//wait for there to be a KEY_NONE before accepting a new key.
			oldkey = key;
		}
	}  
}

void doKeyAction(unsigned int key){
	if(key == KEY_NONE){
        return;
    }

	if(key == KEY_SELECT){
		if(uiState == MAIN){
			uiState = BOLUS_MENU;
		}
		else if(BOLUS_MENU){
			uiState = MAIN;
		}
	}

	String s1; //upper line
	String s2; //lower line
	
	if(uiState == MAIN){
		if(key == KEY_LEFT){
			s2 = (String("Pull ") + decToString(mLBolus) + String(" mL"));
			bolus(PULL);
		}
		if(key == KEY_RIGHT){
			s2 = (String("Push ") + decToString(mLBolus) + String(" mL"));
			bolus(PUSH);
		}
		if(key == KEY_UP){
			mLBolus += mLBolusStep;
		}
		if(key == KEY_DOWN){
			if((mLBolus - mLBolusStep) > 0){
			  mLBolus -= mLBolusStep;
			}
			else{
			  mLBolus = 0;
			}
		}
		s1 = String("Used ") + decToString(mLUsed) + String(" mL");
		s2 = (String("Bolus ") + decToString(mLBolus) + String(" mL"));		
	}
	else if(uiState == BOLUS_MENU){
		if(key == KEY_LEFT){
			//nothin'
		}
		if(key == KEY_RIGHT){
			//nothin'
		}
		if(key == KEY_UP){
			if(mLBolusStepIdx < mLBolusStepsLength-1){
				mLBolusStepIdx++;
				mLBolusStep = mLBolusSteps[mLBolusStepIdx];
			}
		}
		if(key == KEY_DOWN){
			if(mLBolusStepIdx > 0){
				mLBolusStepIdx -= 1;
				mLBolusStep = mLBolusSteps[mLBolusStepIdx];
			}
		}
		s1 = String("Menu> BolusStep");
		s2 = decToString(mLBolusStep);
	}

	//update screen
	lcd.clear();

	s2.toCharArray(charBuf, 16);
	lcd.cursorTo(2, 0);  //line=2, x=0
	lcd.printIn(charBuf);
	
	s1.toCharArray(charBuf, 16);
	lcd.cursorTo(1, 0);  //line=1, x=0
	lcd.printIn(charBuf);
		
	
	//debugging - write character ADC
	/*
        lcd.cursorTo(1, 0);  //line=2, x=0
	String s = String("KEY_ADC: ") + String(adc_key_in);
	s.toCharArray(charBuf, 16);
	lcd.printIn(charBuf);  //line=2, x=0
        */	
}


// Convert ADC value to key number
int get_key(unsigned int input){
  int k;
  for (k = 0; k < NUM_KEYS; k++){
    if (input < adc_key_val[k]){
      return k;
    }
  }
  if (k >= NUM_KEYS){
    k = KEY_NONE;     // No valid key pressed
  }
  return k;
}

String decToString(float decNumber){
	//not a general use converter! Just good for the numbers we're working with here.
	int wholePart = decNumber; //truncate
	int decPart = round(abs(decNumber*1000)-abs(wholePart*1000)); //3 decimal places
        String strZeros = String("");
        if(decPart < 10){
          strZeros = String("00");
        }  
        else if(decPart < 100){
          strZeros = String("0");
        }
	return String(wholePart) + String('.') + strZeros + String(decPart);
}

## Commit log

2014-08-21 Added 3D files and organized
    [nemaMount.scad, nemaMount.stl, rodMountBarrel.scad, rodMountBarrel.stl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]
2014-08-25 Minor tweaks to 3D files to make them a bit nicer
    [rodMountBarrel.scad, rodMountBarrel.stl, rodMountPlunger.scad, rodMountPlunger.stl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]
2014-08-25 Added serial control, added screen updates for triggered mode, removed legacy code, minor 3D file updates.
    [rodMountPlunger.scad, rodMountPlunger.stl]
2014-10-21 minor improvements across the board
    [nemaMount.stl, rodMountBarrel.scad, rodMountBarrel.stl, rodMountPlunger.scad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]
2014-12-18 Added wiring diagram to documentation
    [12v-easyDriver.fzz]
2015-05-30 nut depth was too tight
    [rodMountPlunger.scad]
2015-06-01 updated STLs with correct hole size for nut
    [rodMountPlunger.stl]
2015-06-05 removed old sections of code
    [rodMountBarrel.scad]
2015-10-13 Minor alteration to barrel holder to improve durability and pump accuracy
    [rodMountBarrel.scad, rodMountBarrel.stl]
